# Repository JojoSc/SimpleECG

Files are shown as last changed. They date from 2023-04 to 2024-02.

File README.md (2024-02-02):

# SimpleECG
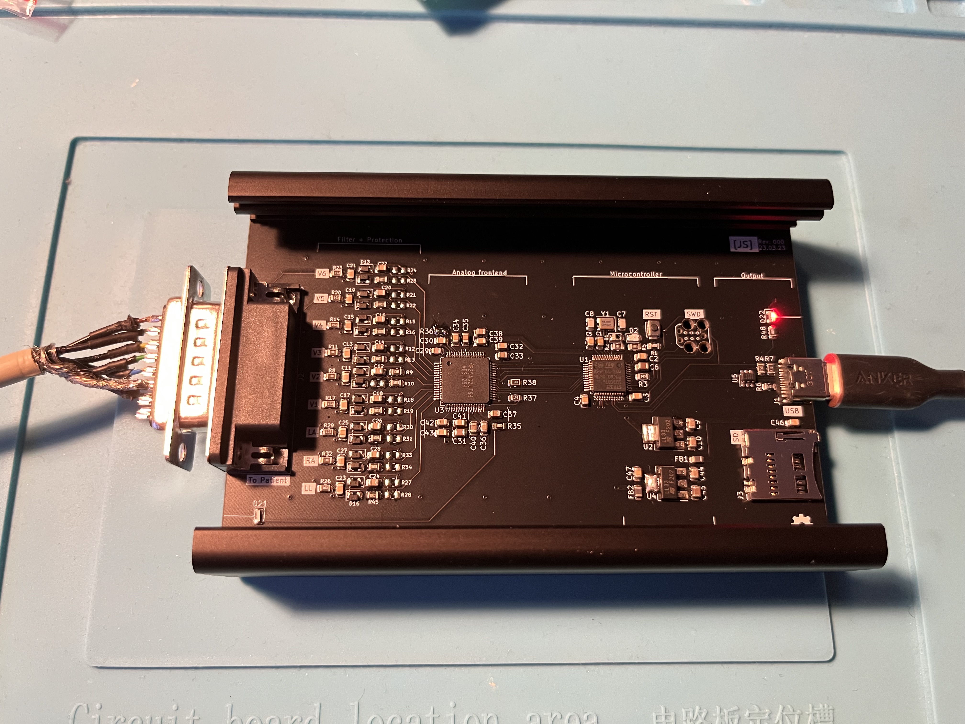
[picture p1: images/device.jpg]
Printed circuit board


This is a USB powered electrocardiograph, which streams the data straight to a computer. Currently it's a barebones version with just some basic protection.

It's a showcase of how easy it is to build your own "medical grade" ECG for ~50$ and should serve you as a starting point if you want to design and build your own. Also, I just really wanted to have an ECG...

**Some key data points:**

- ADS1298 analog frontend
- STM32F103 microprocessor
- USB power and data
- basic filtering and protection between patient and device, but no galvanic isolation between USB power source and PCB
- currently up to 2000 samples per second (limited by SPI speed, can be improved)

## Example Data
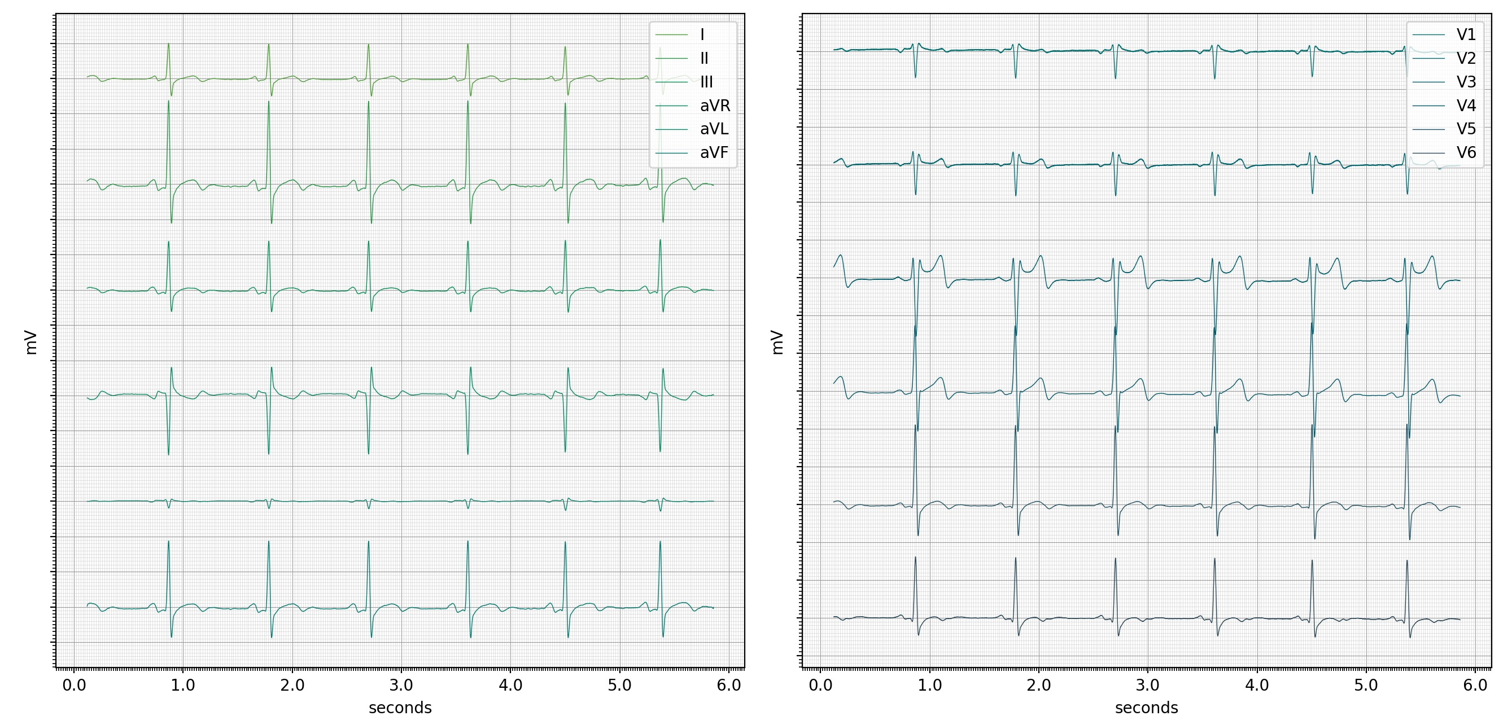
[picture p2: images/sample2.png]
Sample data


## Disclaimer
Don't actually use this in a clinical setting, it is a hobby project and lacks a lot of mandatory safety features for medical devices. For safety reasons I advise only connecting it to a battery powered laptop, which is not connected to an outlet.

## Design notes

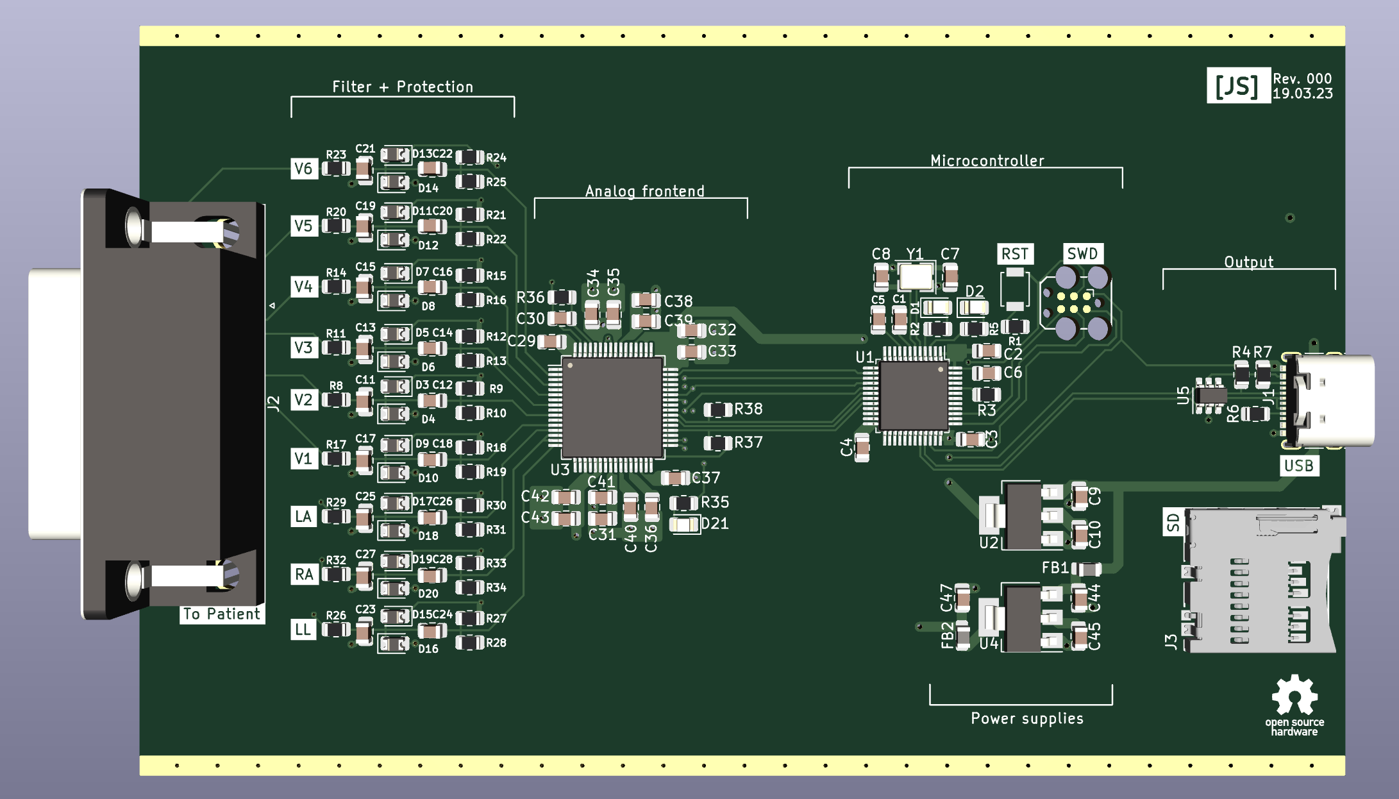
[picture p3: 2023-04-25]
images/board.png

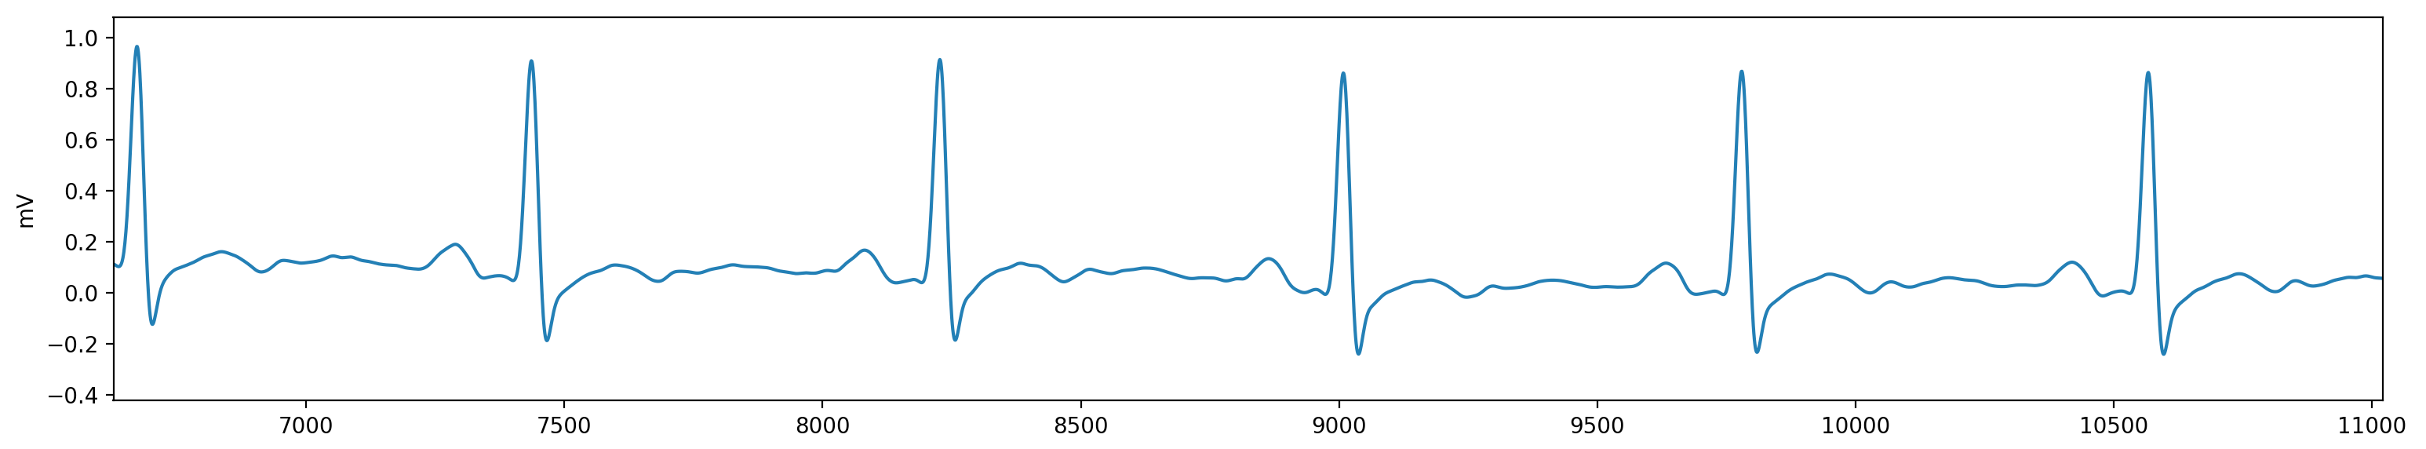
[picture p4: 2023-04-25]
images/sample.png

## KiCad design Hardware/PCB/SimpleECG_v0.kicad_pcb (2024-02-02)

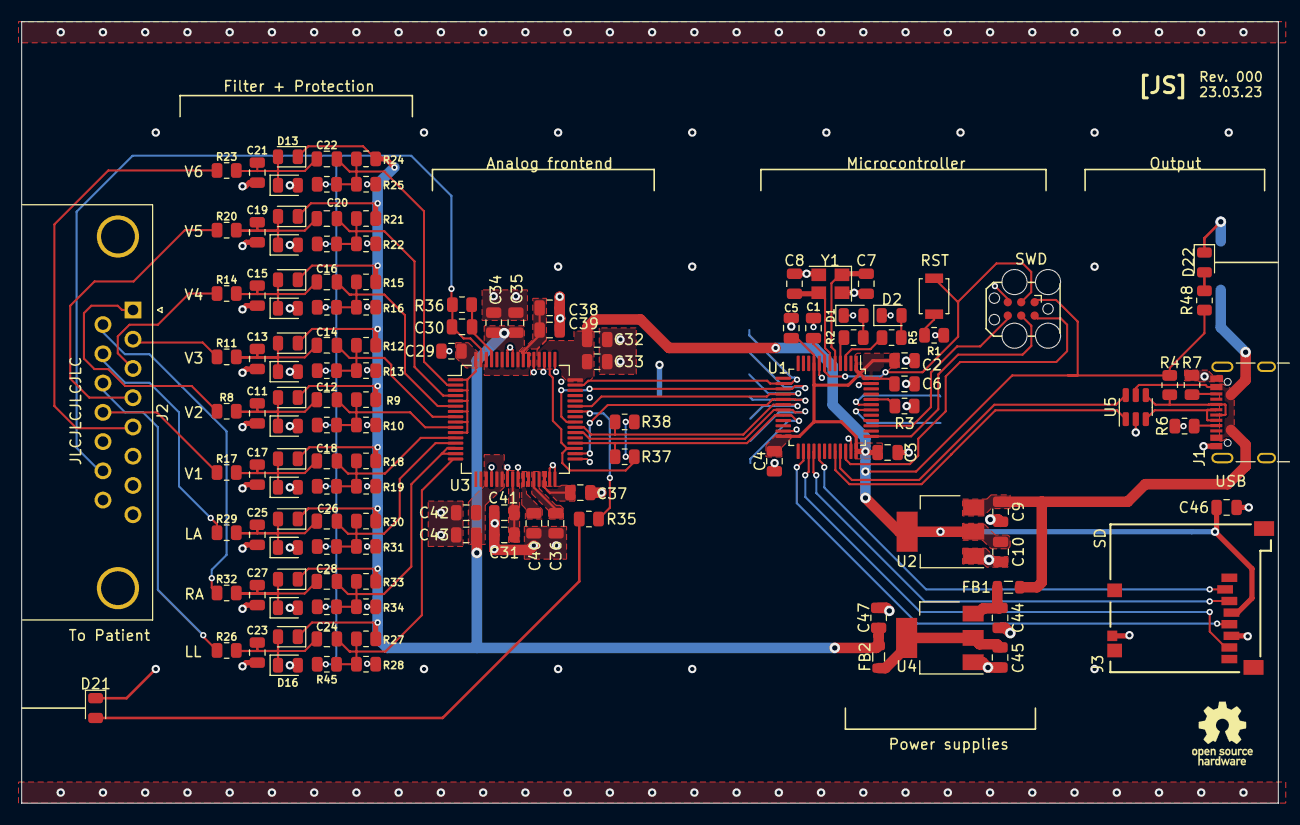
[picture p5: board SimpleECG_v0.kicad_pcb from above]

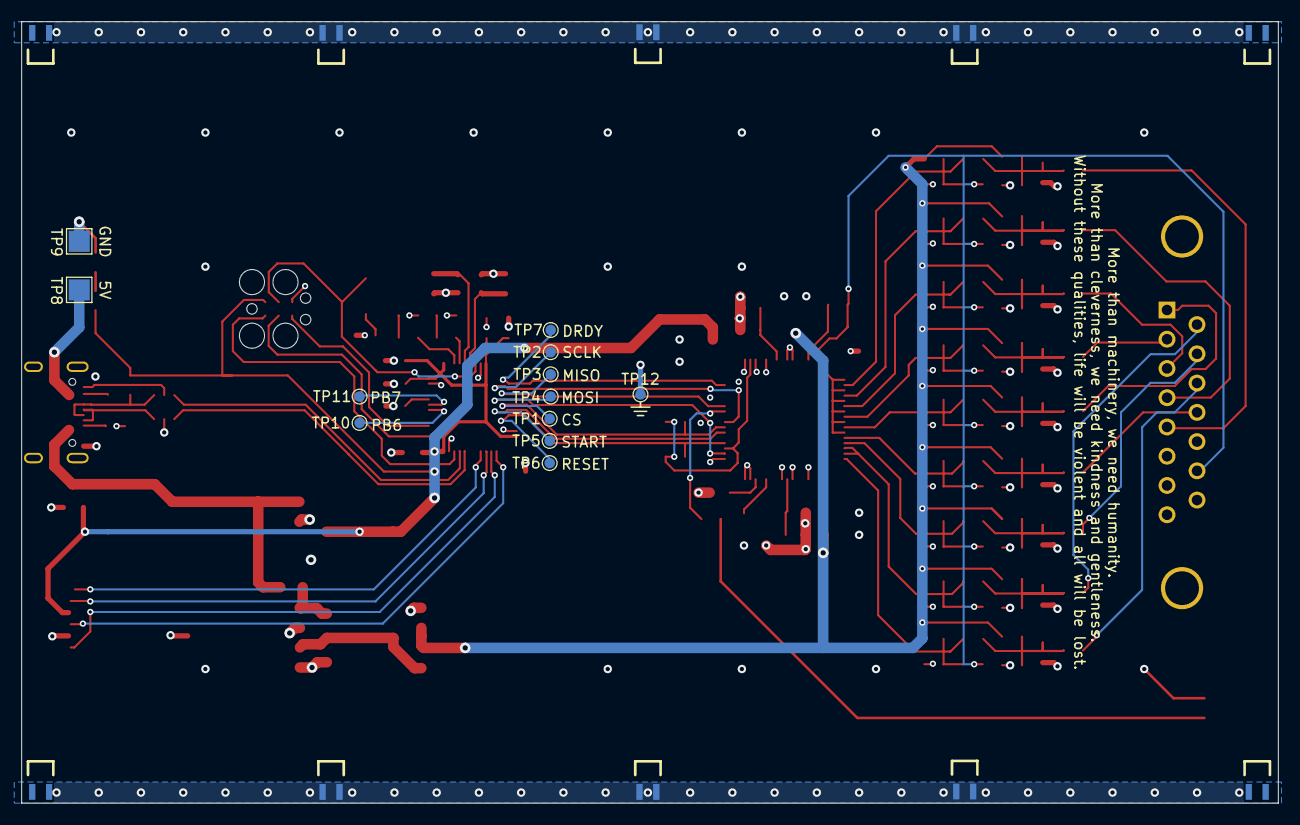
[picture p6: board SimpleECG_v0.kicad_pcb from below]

Board: 4 copper layers, 119.0 x 74.0 mm, 152 parts (22 on the bottom side), 75 nets.

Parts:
C1, C2, C3, C4, C5: 100nF; C_0805_2012Metric
C6: 10uF; C_0805_2012Metric
C7, C8, C11, C12, C13, C14, C15, C16, C17, C18, C19, C20, C21, C22, C23, C24, C25, C26, C27, C28, C29: C; C_0805_2012Metric
C9, C10, C44: 4u7; C_0805_2012Metric
C30: 1.5n; C_0805_2012Metric
C31, C45: 10u; C_0805_2012Metric
C32, C34, C39, C41, C43, C46, C47: 100n; C_0805_2012Metric
C33, C35, C37, C38, C40, C42: 1u; C_0805_2012Metric
C36: 22u; C_0805_2012Metric
D1, D2, D21, D22: LED; LED_0805_2012Metric
D3, D4, D5, D6, D7, D8, D9, D10, D11, D12, D13, D14, D15, D16, D17, D18, D19, D20: D; D_0805_2012Metric
FB1, FB2: FerriteBead; L_0805_2012Metric
J1: USB_C_Receptacle_USB2.0; USB_C_Receptacle_GCT_USB4105-xx-A_16P_TopMnt_Horizontal
J2: Conn_01x15; DSUB-15_Male_Horizontal_P2.77x2.84mm_EdgePinOffset7.70mm_Ho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
J3: Micro_SD_Card; GCT_MEM2051-00-195-00-A
R1, R35, R48: 1k; R_0805_2012Metric
R2, R5: 3.3k; R_0805_2012Metric
R3, R8, R11, R14, R17, R20, R23, R26, R29, R32, R37, R38: 10k; R_0805_2012Metric
R4: 1.5k; R_0805_2012Metric
R6, R7: 5k1; R_0805_2012Metric
R9, R10, R12, R13, R15, R16, R18, R19, R21, R22, R24, R25, R27, R28, R30, R31, R33, R34, R39, R40, R41, R42, R43, R44, R45, R46, R47: R; R_0805_2012Metric
R36: 1M; R_0805_2012Metric
SHLD4, SHLD4#2, SHLD4#3, SHLD4#4, SHLD4#5, SHLD4#6, SHLD4#7, SHLD4#8, SHLD4#9, SHLD4#10: SHLD_FINGER_0820; EMI_SHLD_FINGER_0820
SW1: SW_Push; SW_SPST_B3U-1100P
TC1: TC2030-IDC; Tag-Connect_TC2030-IDC-FP_2x03_P1.27mm_Vertical
TP1, TP2, TP3, TP4, TP5, TP6, TP7: TestPoint_Small; TestPoint_Pad_D1.0mm
TP8, TP9: TestPoint; TestPoint_Pad_2.0x2.0mm
TP10, TP11, TP12: TestPoint; TestPoint_Pad_D1.0mm
U1: STM32F103CBTx; LQFP-48_7x7mm_P0.5mm
U2, U4: AMS1117-3.3; SOT-223-3_TabPin2
U3: ADS1298xPAG; TQFP-64_10x10mm_P0.5mm
U5: SOT-23-6
Y1: 8 MHz; Crystal_SMD_3225-4Pin_3.2x2.5mm

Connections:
+3.3VADC: C34.1, C35.1, C42.1, C43.1, C47.1, D3.1 (K), D5.1 (K), D7.1 (K), D9.1 (K), D11.1 (K), D13.1 (K), D15.1 (K), D17.1 (K), D19.1 (K), FB2.2, R9.1, R12.1, R15.1, R18.1, R21.1, R24.1, R27.1, R30.1, R33.1, U3.19 (AVDD), U3.21 (AVDD), U3.22 (AVDD), U3.54 (AVDD1), U3.56 (AVDD), U3.59 (AVDD), U3.62 (RLDIN)
+3V3: C2.1, C3.1, C4.1, C5.1, C6.1, C10.1, C32.1, C33.1, C46.1, J3.4 (VDD), R4.2, R37.1, R38.1, R48.1, TC1.1 (VCC), U1.1 (VBAT), U1.9 (VDDA), U1.24 (VDD), U1.36 (VDD), U1.48 (VDD), U2.2 (VO), U3.35 (~PWDN), U3.48 (DVDD), U3.50 (DVDD), U3.52 (CLKSEL)
/AFE/ADS_STATUS: R35.1, U3.42 (GPIO1)
/AFE/LA: J2.10, R29.1
/AFE/LA_filtered: C26.2, R30.2, R31.1, R46.2, U3.13 (IN2N)
/AFE/LL: J2.11, R26.1
/AFE/LL_filtered: C24.2, R27.2, R28.1, R45.2, U3.16 (IN1P)
/AFE/MISO: TP3.1, U1.16 (PA6), U3.43 (DOUT)
/AFE/MOSI: TP4.1, U1.17 (PA7), U3.34 (DIN)
/AFE/RA: J2.9, R32.1
/AFE/RA_filtered: C28.2, R33.2, R34.1, R47.2, U3.14 (IN2P), U3.15 (IN1N)
/AFE/SCLK: TP2.1, U1.15 (PA5), U3.40 (SCLK)
/AFE/START: TP5.1, U1.19 (PB1), U3.38 (START)
/AFE/V1: J2.12, R17.1
/AFE/V1_filtered: C18.2, R18.2, R19.1, R42.2, U3.12 (IN3P)
/AFE/V2: J2.1, R8.1
/AFE/V2_filtered: C12.2, R9.2, R10.1, R39.2, U3.10 (IN4P)
/AFE/V3: J2.2, R11.1
/AFE/V3_filtered: C14.2, R12.2, R13.1, R40.2, U3.8 (IN5P)
/AFE/V4: J2.3, R14.1
/AFE/V4_filtered: C16.2, R15.2, R16.1, R41.2, U3.6 (IN6P)
/AFE/V5: J2.4, R20.1
/AFE/V5_filtered: C20.2, R21.2, R22.1, R43.2, U3.4 (IN7N)
/AFE/V6: J2.5, R23.1
/AFE/V6_filtered: C22.2, R24.2, R25.1, R44.2, U3.2 (IN8P)
/AFE/VCAP1: C36.1, U3.28 (VCAP1)
/AFE/VCAP2: C37.1, U3.30 (VCAP2)
/AFE/VCAP3: C38.1, C39.1, U3.55 (VCAP3)
/AFE/VCAP4: C40.1, U3.26 (VCAP4)
/AFE/VREFP: C31.1, C41.1, U3.24 (VREFP)
/AFE/WCT: C29.1, U3.1 (IN8N), U3.3 (IN7P), U3.5 (IN6N), U3.7 (IN5N), U3.9 (IN4N), U3.11 (IN3N), U3.64 (WCT)
/AFE/~CS: R38.2, TP1.1, U1.18 (PB0), U3.39 (~CS)
/AFE/~DRDY: TP7.1, U1.14 (PA4), U3.47 (~DRDY)
/AFE/~RESET: R37.2, TP6.1, U1.20 (PB2), U3.36 (~RESET)
/Power/CC1: J1.A5 (CC1), R6.1
/Power/CC2: J1.B5 (CC2), R7.2
/Power/U_USB_D+: J1.A6 (D+), J1.B6 (D+), R4.1, U5.4 (B_{In})
/Power/U_USB_D-: J1.A7 (D-), J1.B7 (D-), U5.3 (A_{In})
/Power/VBUS: C9.1, FB1.1, J1.A4 (VBUS), J1.A9 (VBUS), J1.B4 (VBUS), J1.B9 (VBUS), TP8.1, U2.3 (VI), U5.5 (V+)
/SD_CS: J3.2 (DAT3/CD), U1.29 (PA8)
/SPI2_CLK: J3.5 (CLK), U1.26 (PB13)
/SPI2_MISO: J3.7 (DAT0), U1.27 (PB14)
/SPI2_MOSI: J3.3 (CMD), U1.28 (PB15)
/STM32F1/BOOT0: R3.2, U1.44 (BOOT0)
/STM32F1/ERROR_LED: R5.1, U1.3 (PC14)
/STM32F1/NRST: C1.1, SW1.2, TC1.3 (NRESET), U1.7 (NRST)
/STM32F1/OSC_IN: C7.1, U1.5 (PD0), Y1.1
/STM32F1/OSC_OUT: C8.1, U1.6 (PD1), Y1.3
/STM32F1/PB6: TP10.1, U1.42 (PB6)
/STM32F1/PB7: TP11.1, U1.43 (PB7)
/STM32F1/STATUS_LED: R2.1, U1.4 (PC15)
/STM32F1/SWCLK: TC1.4 (SWCLK), U1.37 (PA14)
/STM32F1/SWDIO: TC1.2 (SWDIO), U1.34 (PA13)
/STM32F1/SWSWO: TC1.6 (SWO), U1.39 (PB3)
GND: C1.2, C2.2, C3.2, C4.2, C5.2, C6.2, C7.2, C8.2, C9.2, C10.2, C11.2, C13.2, C15.2, C17.2, C19.2, C21.2, C23.2, C25.2, C27.2, C29.2, C31.2, C32.2, C33.2, C34.2, C35.2, C36.2, C37.2, C38.2, C39.2, C40.2, C41.2, C42.2, C43.2, C44.2, C45.2, C46.2, C47.2, D1.1 (K), D2.1 (K), D4.2 (A), D6.2 (A), D8.2 (A), D10.2 (A), D12.2 (A), D14.2 (A), D16.2 (A), D18.2 (A), D20.2 (A), D21.1 (K), D22.1 (K), J1.A1 (GND), J1.A12 (GND), J1.B1 (GND), J1.B12 (GND), J2.6, J3.6 (VSS), J3.9 (SHIELD), R1.1, R3.1, R6.2, R7.1, R10.2, R13.2, R16.2, R19.2, R22.2, R25.2, R28.2, R31.2, R34.2, SHLD4.1, SHLD4#2.1, SHLD4#3.1, SHLD4#4.1, SHLD4#5.1, SHLD4#8.1, TC1.5 (GND), TP9.1, TP12.1, U1.8 (VSSA), U1.23 (VSS), U1.35 (VSS), U1.47 (VSS), U2.1 (GND), U3.20 (AVSS), U3.23 (AVSS), U3.25 (VREFN), U3.31 (RESV1), U3.32 (AVSS), U3.33 (DGND), U3.49 (DGND), U3.51 (DGND), U3.53 (AVSS1), U3.57 (AVSS), U3.58 (AVSS), U4.1 (GND), U5.2 (V-), Y1.2, Y1.4
unnamed: D1.2 (A), R2.2
unnamed: D2.2 (A), R5.2
unnamed: C11.1, C12.1, D3.2 (A), D4.1 (K), R8.2
unnamed: C13.1, C14.1, D5.2 (A), D6.1 (K), R11.2
unnamed: C15.1, C16.1, D7.2 (A), D8.1 (K), R14.2
unnamed: C17.1, C18.1, D9.2 (A), D10.1 (K), R17.2
unnamed: C19.1, C20.1, D11.2 (A), D12.1 (K), R20.2
unnamed: C21.1, C22.1, D13.2 (A), D14.1 (K), R23.2
unnamed: C23.1, C24.1, D15.2 (A), D16.1 (K), R26.2
unnamed: C25.1, C26.1, D17.2 (A), D18.1 (K), R29.2
unnamed: C27.1, C28.1, D19.2 (A), D20.1 (K), R32.2
unnamed: D21.2 (A), R35.2
unnamed: D22.2 (A), R48.2
unnamed: R1.2, SW1.1
unnamed: C30.2, R36.2, U3.61 (RLDINV)
unnamed: C44.1, FB1.2, U4.3 (VI)
unnamed: C45.1, FB2.1, U4.2 (VO)
RL: C30.1, J2.14, R36.1, R39.1, R40.1, R41.1, R42.1, R43.1, R44.1, R45.1, R46.1, R47.1, U3.63 (RLDOUT)
USB_D+: U1.33 (PA12), U5.6 (B_{Out})
USB_D-: U1.32 (PA11), U5.1 (A_{OUT})

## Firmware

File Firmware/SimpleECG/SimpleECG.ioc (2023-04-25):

#MicroXplorer Configuration settings - do not modify
File.Version=6
KeepUserPlacement=false
Mcu.Family=STM32F1
Mcu.IP0=NVIC
Mcu.IP1=RCC
Mcu.IP2=SPI1
Mcu.IP3=SYS
Mcu.IP4=USB
Mcu.IP5=USB_DEVICE
Mcu.IPNb=6
Mcu.Name=STM32F103C(8-B)Tx
Mcu.Package=LQFP48
Mcu.Pin0=PC14-OSC32_IN
Mcu.Pin1=PC15-OSC32_OUT
Mcu.Pin10=PB2
Mcu.Pin11=PA11
Mcu.Pin12=PA12
Mcu.Pin13=PA13
Mcu.Pin14=PA14
Mcu.Pin15=VP_SYS_VS_Systick
Mcu.Pin16=VP_USB_DEVICE_VS_USB_DEVICE_CDC_FS
Mcu.Pin2=PD0-OSC_IN
Mcu.Pin3=PD1-OSC_OUT
Mcu.Pin4=PA4
Mcu.Pin5=PA5
Mcu.Pin6=PA6
Mcu.Pin7=PA7
Mcu.Pin8=PB0
Mcu.Pin9=PB1
Mcu.PinsNb=17
Mcu.ThirdPartyNb=0
Mcu.UserConstants=
Mcu.UserName=STM32F103CBTx
MxCube.Version=6.4.0
MxDb.Version=DB.6.0.40
NVIC.BusFault_IRQn=true\:0\:0\:false\:false\:true\:false\:false
NVIC.DebugMonitor_IRQn=true\:0\:0\:false\:false\:true\:false\:false
NVIC.ForceEnableDMAVector=true
NVIC.HardFault_IRQn=true\:0\:0\:false\:false\:true\:false\:false
NVIC.MemoryManagement_IRQn=true\:0\:0\:false\:false\:true\:false\:false
NVIC.NonMaskableInt_IRQn=true\:0\:0\:false\:false\:true\:false\:false
NVIC.PendSV_IRQn=true\:0\:0\:false\:false\:true\:false\:false
NVIC.PriorityGroup=NVIC_PRIORITYGROUP_4
NVIC.SVCall_IRQn=true\:0\:0\:false\:false\:true\:false\:false
NVIC.SysTick_IRQn=true\:15\:0\:false\:false\:true\:false\:true
NVIC.USB_LP_CAN1_RX0_IRQn=true\:0\:0\:false\:false\:true\:false\:true
NVIC.UsageFault_IRQn=true\:0\:0\:false\:false\:true\:false\:false
PA11.Mode=Device
PA11.Signal=USB_DM
PA12.Mode=Device
PA12.Signal=USB_DP
PA13.Mode=Serial_Wire
PA13.Signal=SYS_JTMS-SWDIO
PA14.Mode=Serial_Wire
PA14.Signal=SYS_JTCK-SWCLK
PA4.GPIOParameters=GPIO_Label
PA4.GPIO_Label=nDRDY
PA4.Locked=true
PA4.Signal=GPIO_Input
PA5.Mode=Full_Duplex_Master
PA5.Signal=SPI1_SCK
PA6.Mode=Full_Duplex_Master
PA6.Signal=SPI1_MISO
PA7.Mode=Full_Duplex_Master
PA7.Signal=SPI1_MOSI
PB0.GPIOParameters=GPIO_Label
PB0.GPIO_Label=nCS
PB0.Locked=true
PB0.Signal=GPIO_Output
PB1.GPIOParameters=GPIO_Label
PB1.GPIO_Label=START
PB1.Locked=true
PB1.Signal=GPIO_Output
PB2.GPIOParameters=GPIO_Label
PB2.GPIO_Label=nRESET
PB2.Locked=true
PB2.Signal=GPIO_Output
PC14-OSC32_IN.GPIOParameters=GPIO_Label
PC14-OSC32_IN.GPIO_Label=LED_ERROR
PC14-OSC32_IN.Locked=true
PC14-OSC32_IN.Signal=GPIO_Output
PC15-OSC32_OUT.GPIOParameters=GPIO_Label
PC15-OSC32_OUT.GPIO_Label=LED_STATUS
PC15-OSC32_OUT.Locked=true
PC15-OSC32_OUT.Signal=GPIO_Output
PD0-OSC_IN.Mode=HSE-External-Oscillator
PD0-OSC_IN.Signal=RCC_OSC_IN
PD1-OSC_OUT.Mode=HSE-External-Oscillator
PD1-OSC_OUT.Signal=RCC_OSC_OUT
PinOutPanel.RotationAngle=0
ProjectManager.AskForMigrate=true
ProjectManager.BackupPrevious=false
ProjectManager.CompilerOptimize=6
ProjectManager.ComputerToolchain=false
ProjectManager.CoupleFile=false
ProjectManager.CustomerFirmwarePackage=
ProjectManager.DefaultFWLocation=true
ProjectManager.DeletePrevious=true
ProjectManager.DeviceId=STM32F103CBTx
ProjectManager.FirmwarePackage=STM32Cube FW_F1 V1.8.4
ProjectManager.FreePins=false
ProjectManager.HalAssertFull=false
ProjectManager.HeapSize=0x200
ProjectManager.KeepUserCode=true
ProjectManager.LastFirmware=true
ProjectManager.LibraryCopy=1
ProjectManager.MainLocation=Core/Src
ProjectManager.NoMain=false
ProjectManager.PreviousToolchain=
ProjectManager.ProjectBuild=false
ProjectManager.ProjectFileName=SimpleECG.ioc
ProjectManager.ProjectName=SimpleECG
ProjectManager.RegisterCallBack=
ProjectManager.StackSize=0x400
ProjectManager.TargetToolchain=STM32CubeIDE
ProjectManager.ToolChainLocation=
ProjectManager.UnderRoot=true
ProjectManager.functionlistsort=1-SystemClock_Config-RCC-false-HAL-false,2-MX_GPIO_Init-GPIO-false-HAL-true,3-MX_USB_DEVICE_Init-USB_DEVICE-false-HAL-false,4-MX_SPI1_Init-SPI1-false-HAL-true
RCC.ADCFreqValue=24000000
RCC.AHBFreq_Value=48000000
RCC.APB1CLKDivider=RCC_HCLK_DIV2
RCC.APB1Freq_Value=24000000
RCC.APB1TimFreq_Value=48000000
RCC.APB2Freq_Value=48000000
RCC.APB2TimFreq_Value=48000000
RCC.FCLKCortexFreq_Value=48000000
RCC.FamilyName=M
RCC.HCLKFreq_Value=48000000
RCC.IPParameters=ADCFreqValue,AHBFreq_Value,APB1CLKDivider,APB1Freq_Value,APB1TimFreq_Value,APB2Freq_Value,APB2TimFreq_Value,FCLKCortexFreq_Value,FamilyName,HCLKFreq_Value,MCOFreq_Value,PLLCLKFreq_Value,PLLMCOFreq_Value,PLLMUL,SYSCLKFreq_VALUE,SYSCLKSource,TimSysFreq_Value,USBFreq_Value,VCOOutput2Freq_Value
RCC.MCOFreq_Value=48000000
RCC.PLLCLKFreq_Value=48000000
RCC.PLLMCOFreq_Value=24000000
RCC.PLLMUL=RCC_PLL_MUL6
RCC.SYSCLKFreq_VALUE=48000000
RCC.SYSCLKSource=RCC_SYSCLKSOURCE_PLLCLK
RCC.TimSysFreq_Value=48000000
RCC.USBFreq_Value=48000000
RCC.VCOOutput2Freq_Value=8000000
SPI1.BaudRatePrescaler=SPI_BAUDRATEPRESCALER_4
SPI1.CLKPhase=SPI_PHASE_2EDGE
SPI1.CalculateBaudRate=12.0 MBits/s
SPI1.Direction=SPI_DIRECTION_2LINES
SPI1.IPParameters=VirtualType,Mode,Direction,BaudRatePrescaler,CalculateBaudRate,CLKPhase
SPI1.Mode=SPI_MODE_MASTER
SPI1.VirtualType=VM_MASTER
USB_DEVICE.CLASS_NAME_FS=CDC
USB_DEVICE.IPParameters=VirtualMode,VirtualModeFS,CLASS_NAME_FS
USB_DEVICE.VirtualMode=Cdc
USB_DEVICE.VirtualModeFS=Cdc_FS
VP_SYS_VS_Systick.Mode=SysTick
VP_SYS_VS_Systick.Signal=SYS_VS_Systick
VP_USB_DEVICE_VS_USB_DEVICE_CDC_FS.Mode=CDC_FS
VP_USB_DEVICE_VS_USB_DEVICE_CDC_FS.Signal=USB_DEVICE_VS_USB_DEVICE_CDC_FS
board=custom
isbadioc=false

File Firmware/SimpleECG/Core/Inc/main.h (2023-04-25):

/* USER CODE BEGIN Header */
/**
  ******************************************************************************
  * @file           : main.h
  * @brief          : Header for main.c file.
  *                   This file contains the common defines of the application.
  ******************************************************************************
  * @attention
  *
  * Copyright (c) 2023 STMicroelectronics.
  * All rights reserved.
  *
  * This software is licensed under terms that can be found in the LICENSE file
  * in the root directory of this software component.
  * If no LICENSE file comes with this software, it is provided AS-IS.
  *
  ******************************************************************************
  */
/* USER CODE END Header */

/* Define to prevent recursive inclusion -------------------------------------*/
#ifndef __MAIN_H
#define __MAIN_H

#ifdef __cplusplus
extern "C" {
#endif

/* Includes ------------------------------------------------------------------*/
#include "stm32f1xx_hal.h"

/* Private includes ----------------------------------------------------------*/
/* USER CODE BEGIN Includes */

/* USER CODE END Includes */

/* Exported types ------------------------------------------------------------*/
/* USER CODE BEGIN ET */

/* USER CODE END ET */

/* Exported constants --------------------------------------------------------*/
/* USER CODE BEGIN EC */

/* USER CODE END EC */

/* Exported macro ------------------------------------------------------------*/
/* USER CODE BEGIN EM */

/* USER CODE END EM */

/* Exported functions prototypes ---------------------------------------------*/
void Error_Handler(void);

/* USER CODE BEGIN EFP */

/* USER CODE END EFP */

/* Private defines -----------------------------------------------------------*/
#define LED_ERROR_Pin GPIO_PIN_14
#define LED_ERROR_GPIO_Port GPIOC
#define LED_STATUS_Pin GPIO_PIN_15
#define LED_STATUS_GPIO_Port GPIOC
#define nDRDY_Pin GPIO_PIN_4
#define nDRDY_GPIO_Port GPIOA
#define nCS_Pin GPIO_PIN_0
#define nCS_GPIO_Port GPIOB
#define START_Pin GPIO_PIN_1
#define START_GPIO_Port GPIOB
#define nRESET_Pin GPIO_PIN_2
#define nRESET_GPIO_Port GPIOB
/* USER CODE BEGIN Private defines */

/* USER CODE END Private defines */

#ifdef __cplusplus
}
#endif

#endif /* __MAIN_H */

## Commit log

2024-02-02 First working version, with 12-lead recording
    [Backplate.kicad_pcb, Backplate.kicad_sch, Electrode_Filtering.kicad_sch, Frontplate.kicad_pcb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]
2024-02-02 Added sample image
